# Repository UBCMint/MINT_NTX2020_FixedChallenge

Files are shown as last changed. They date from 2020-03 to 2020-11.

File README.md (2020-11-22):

# MINT EEG Acquisition System: JellyFish 1.0

## Background
There are many commercially available EEG headsets such as MUSE, OpenBCI, Neurosky, and Emotiv. However, they have too high price, not enough electrodes for high EEG spatial-resolution, low signal quality, or too much time to set up. Over the last two years, MINT has mainly focused on the EEG board only. This year, we will integrate the EEG board into a complete EEG headset that is comfortable, adjustable, sturdy to be worn anytime and anywhere at a reasonable price so that EEG headset can become a common household device as a computer mouse.

## Overall Design

## Headset Design
One of the primary issues that needed to be tackled was being able to adjust the headset to various headsizes. On top of this, our headset needed to be able to conform to the 10-20 system for electrode placement. This was done by using three headbands that go across the head. These headbands each contain rails which the electrodes lock onto. Additionally, to deal with the various head circumferences available, an elastic band is placed across the forehead, attaching the two ends of the headset, allowing for various headsizes to be used with different elastic bands and allowing the headset remain stable. This allows for the electrodes to be placed anywhere along the head thus conforming to all head sizes.

In our final design it was determined that a fluid source was needed to ensure that the electrodes were saturated at all times in order to deliver the best result. This was done by creating a tank at the top of the head which holds said fluid. One key concern of having this fluid was that we knew that it would conduct the signal throughout the solution and with that, we needed to design a system that not only held the fluid but also distributed the solution separately to each electrode. From this, it was determined that a rotating mechanism was the best solution in that every couple hours an individual would need to rotate the lid to the holder in order to distribute the fluid.

In addition to the central fluid tank holder, another method for solution distribution has been made. In this solution, rather than having tubes branching from a central tank, each electrode would possess its own mini-tank that would easily connect and disconnect to refill (similar to filling a toy water gun). This method requires more testing. However if successful, may allow for more fluid to be stored in the system as a whole.

The final aspect to this headset is the board holder located in the back of the head. This unit combines both the battery for the circuit as well as the circuit board in a protected location with holes conveniently located for any required connections or buttons. Additionally, this boardbox will be wrapped in sheet metal to minimize any electromagnetic radiation that may be present in the area. This allows all processing and power of the headset to be located in one location. 

## Electrode
The wet electrode consists of a piece of cotton sandwich between the scalp and the pre-amplifier PCB board that acts as a bridge when saturated with the electrode solution. Active electrodes with pre-amplifiers allow for the signal acquired to be immediately boosted before additional noise is incorporated into the signal during the travel between the electrode and the system. The signal can be further increased by a screw on top of the electrode that increases the pressure between the cotton and the scalp when twisted. Handles on the sides of the electrode allows for the component to be mounted and slide on the headset frame for maximum flexibility.

## EEG Board: MENTHA 3.0

## Budget
Below is the rough breakdown of costs, for those who want to replicate this design:  
~$0.5 for consumable cotton pieces and salt.  
~$1.50 for fluid tank & board holder (PLA)  
~$0.12 for each electrode (PLA)  
~$3.25 for headset frame (TPU)  

## About Us

JellyFish 1.0 was created by [(Multifaceted Innovation in NeuroTechnology](https://ubcmint.github.io/) (MINT), an undergraduate neurotech team, part of the group [Biomedical Engineering Student Team](http://www.ubcbest.com/) at the University of British Columbia in Vancouver, Canada.

JellyFish 1.0 was submitted as a project for the Fixed Challenge category of the [NeuroTechX 2020 Student Club competition](https://neurotechx.github.io/studentclubs/competition/).

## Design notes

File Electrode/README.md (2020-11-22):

# MINT EEG Electrode Evolution Summary 

## Electroplated Electrodes (Dry)
The electroplating electrodes use a mixture of Ag/AgCl or silver paint  (SCP03B) solution to plate the surface of the electrodes. Several electrode shapes and designs were explored to determine optimal configuration for effective signal collection and high signal:noise reading. These electrodes can record alpha rhythms correctly, but it has been noted that signals collected by the electrodes have a higher noise and impedance compared to the traditional Ag/AgCl electrodes. Additionally, coating begins to wear off after approximately 100 scratches. The scratches can be remend by recoating the electrodes with the silver solution. Although electroplated electrodes can measure alpha waves, the concept was abandoned due to its low signal:noise ratio and durability.

## Regenerated Cellulose Membranes Electrodes (Dry)
Regenerated cellulose membrane electrodes are identified to be suitable for long term use due to regenerative properties as well as high porosity for high surface area. Flower paper was identified to have regenerated cellulose membrane properties. The electrodes were soaked in an electrolyte solution of eight packs of table salt dissolved in water. After conducting eight impedance measurements, a high impedance average was found. Due to the identified high impedance, the regenerated cellulose membrane electrodes were not fully developed. 

## Conductive Fabric Electrodes (Dry)
The developed conductive fabric electrode electrodes use a 3x3x1.5cm cube packaging foam as a core, wrapped in a sheet of woven, silver, conductive fabric. The electrode provides comfort to the user as well as allowing electrodes to contour the head. However, the fabric electrode was calculated to have high impedance in addition to visual wear-and-tears to the fabric. Despite the comfortability and contouring capabilities, the conductive fabric electrodes were not fully developed due to a high impedance and low durability.

## Dry Spring Electrodes (Dry)
Dry spring electrodes incorporated springs into dry finger electrodes to better contour the head. Samples from an MDPI article were requested to analyze spring electrodes. Upon testing, the required pressure and flexibility could not be achieved and the electrodes were deemed to be uncomfortable or painful. Although impedance was not recorded, the idea was scrapped due to high discomfortability from high spring constant.

## Compression Fabric Electrodes (Dry)
Similar to the conductive fabric, a pressure-sensitive conductive sheet (velostat/linqstat) is used in lieu of the conductive fabric. The conductive material has a resistance reducing property when pressure is applied to the fabric, which can be useful for designing flexible sensors. The pressure also allows the electrode to better contour to the head and maximize surface area for signal acquisition. However, upon testing, the compression fabric is found to be twice as large as the conductive fabric, despite applying large pressure. Additionally, after several uses, oily residue begins to accumulate on the surface of the fabric. This suggests a quick and easy formation of biofilms, which may require additional maintenance from the user. Failure to manage the electrodes may impose health risk onto the user. Therefore, the compression fabric is rejected due to its high impedance and potential health issues.

## Cotton Electrodes (Hybrid)
The current design looks at creating a hybrid electrode which uses cotton and electrolyte solution to bridge the connection between the scalp and PCB board. The cotton will be connected to a water tank that contains dissolved salt. Adding pressure onto the cotton allows more of the liquid to spread onto the scalp, maximizing surface area for signal acquisition. Conducting impedance tests show that cotton soaked in solution has a significantly lower impedance than dry or wet OPENBCI electrodes. Therefore, the hybrid cotton electrodes were further developed for the 2020 MINT EEG acquisition system. 

## Extensive writeup of past designs can be found on the [team’s Google Drive](https://docs.google.com/document/d/16VlDZtCEF2bn4U8mC6i96VPIYXMff-jvLBDzw5MMWTI/edit#heading=h.276hzmhpmpdi)

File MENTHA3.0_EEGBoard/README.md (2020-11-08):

# MINT_EEGBoard: MENTHA 3.0

### Background
The goal of MENTHA is to design a board that can collect EEG potentials accurately and effectively. MENTHA 3.0 will utilize a PIC32MX microcontroller to send data acquired from the specialized biopotential measurement device (ADS1299) to a PC, where the data will be analyzed and live plotted.

The choice to use these components were based on research which showed the prevalence of the ADS1299 in literature. Additionally, MINT wanted to develop a smaller and more compact design than previous submissions.

## Electrical

### Initial concept
The initial concept was to use a similar approach as to previous years. That being implementing instrumentation amplifiers, along with active filters in order to acquire our signal. 

After testing with various amplifiers and topologies, performing some research, and receiving input from colleagues, the choice was made to use the ADS1299 chip with passive and software filters instead. The ADS1299 is low noise and can measure small voltages, which is important for biopotential measurements  

### ADS1299
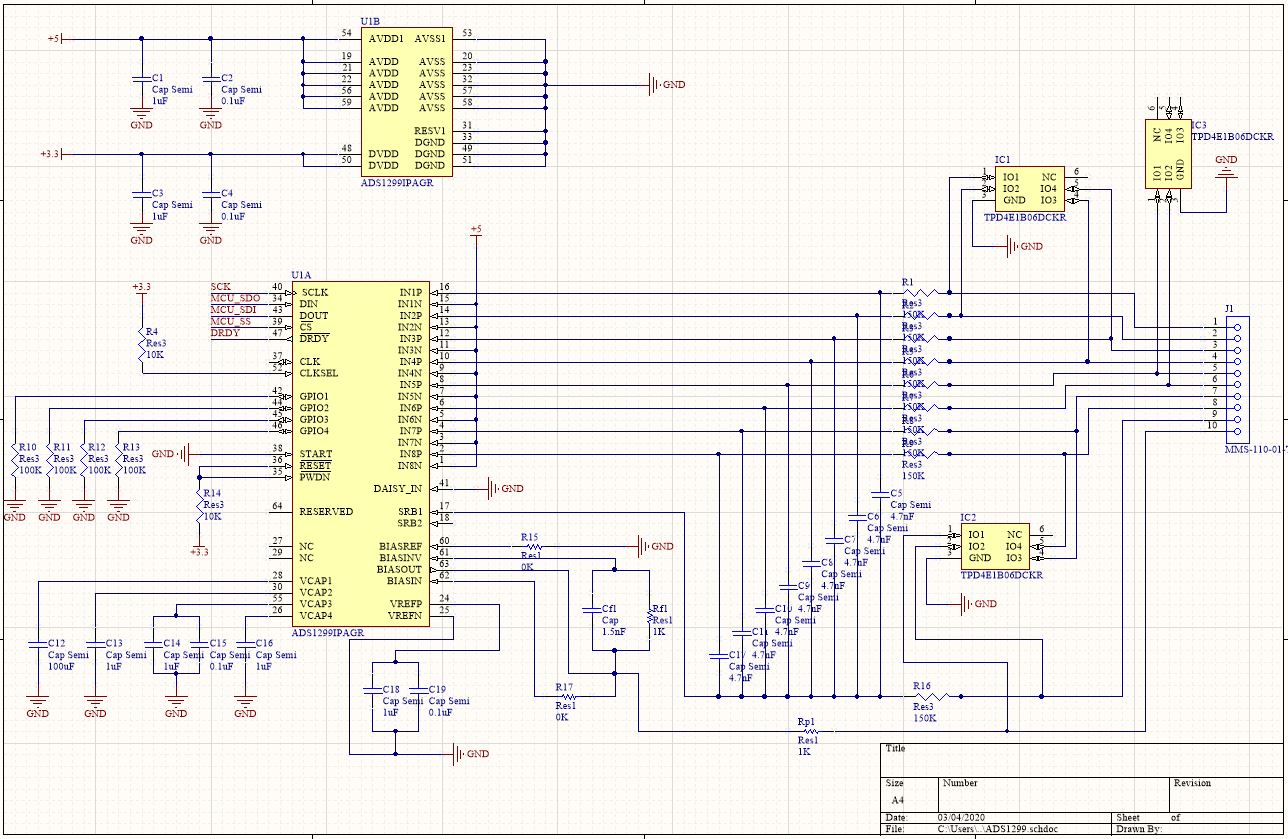
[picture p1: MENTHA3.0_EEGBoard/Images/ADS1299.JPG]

We have set up the ADS 1299 with a referential montage and as such, each of the 8 input channels have the same reference electrode. We implemented a differential passive low pass filter at 160Hz (see bode plot). This lets us remove high frequency signals without introducing more noise to the system or losing signal in 10-50Hz rage. Furthermore, the differential set up of the filter rejects common signals between the electrode signal and the reference ground and therefore removes common noise and DC noise. The ADS1299 is connected to the microcontroller with and SPI interface.

Bode plots and frequency specifics?

### Microcontroller
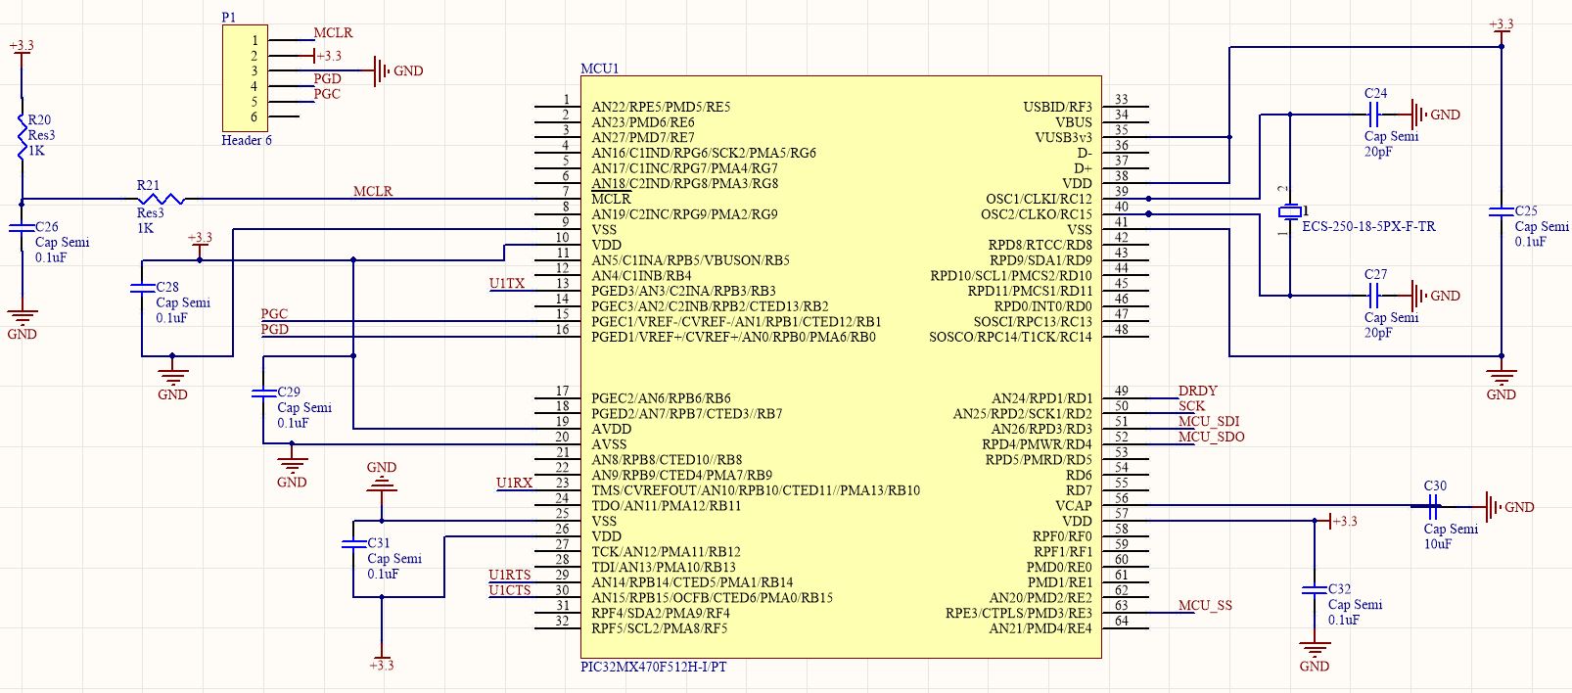
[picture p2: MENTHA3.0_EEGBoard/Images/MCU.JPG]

The PIC32MX450/470 is being utilized for this project. The microcontroller was chosen due to its relatively fast clock speed, large memory size, and numerous peripheral pins. Additionally, Microchip offers easy solutions for programming and debugging using the PICkit3 and their MPLAB X IDE. The device is programmed using the PICKit3 through the pins labeled MCLR, PGD, and PGC. Attached to our MCU we have a 25MHz oscillator to set the clock speed, an FT232R USB UART IC for PC data transfer, connections to the ADS1299 through SPI, and the various required connections and decoupling capacitors.

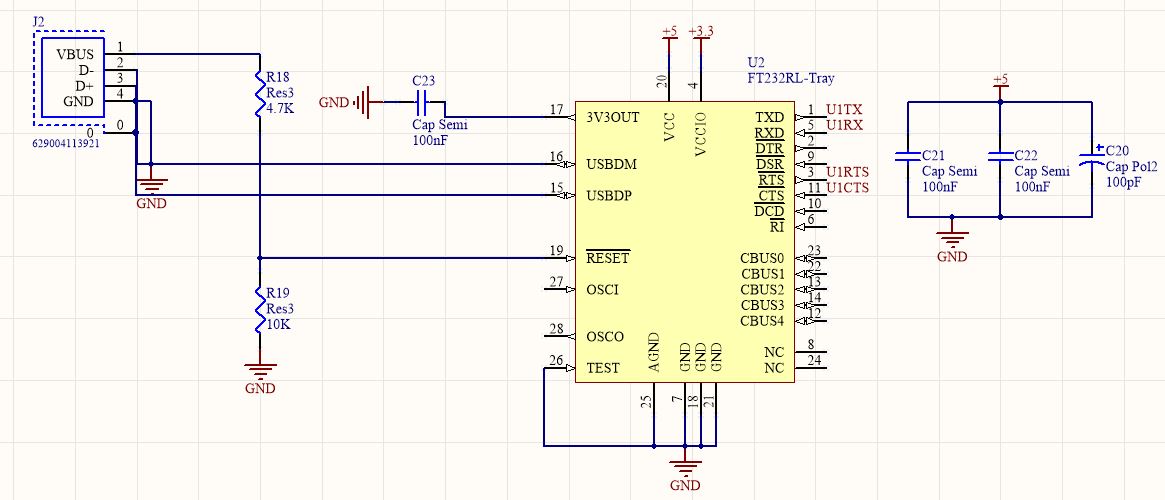
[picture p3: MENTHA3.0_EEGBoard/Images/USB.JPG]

To interface with a PC for data transfer, we have implemented an FT232R USB UART IC. This device connects to the UART peripherals of the PIC32 in order to transfer data to and from a PC with a wired USB-A connection. We have configured the FT232R chip in a self powered configuration as acording to the IC datasheet.

### Power Electronics
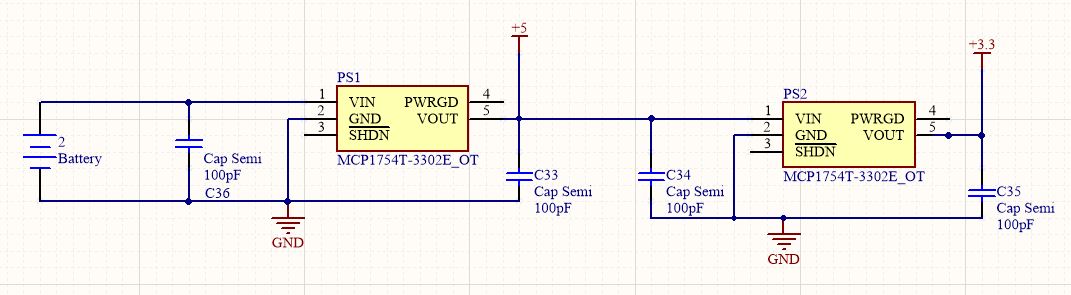
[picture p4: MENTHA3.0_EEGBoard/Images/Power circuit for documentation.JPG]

The Power electronics for the board offers two power rails using two voltage regulators. One is used to create a 5V rail from the input battery or power supply connection. The other is used to create a 3.3V rail and uses the 5V rail as an input.

## PCB Layout
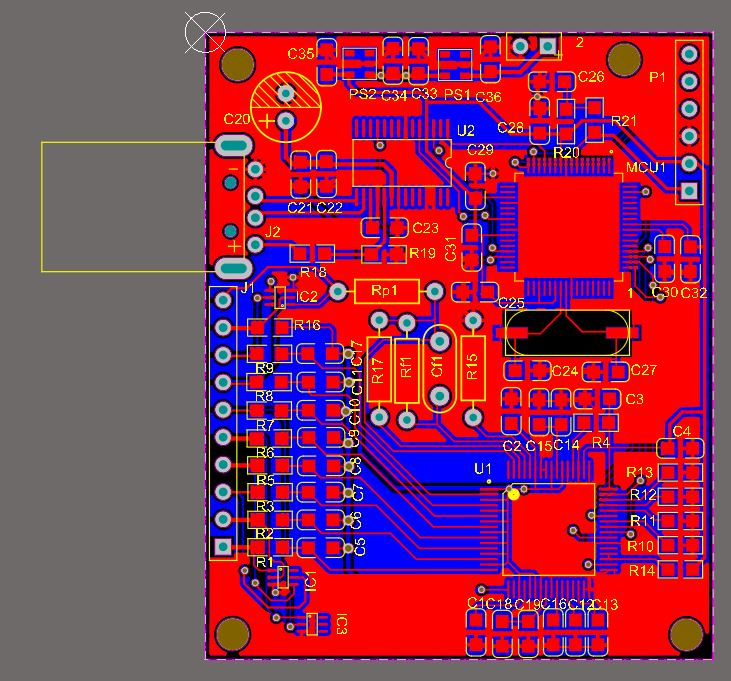
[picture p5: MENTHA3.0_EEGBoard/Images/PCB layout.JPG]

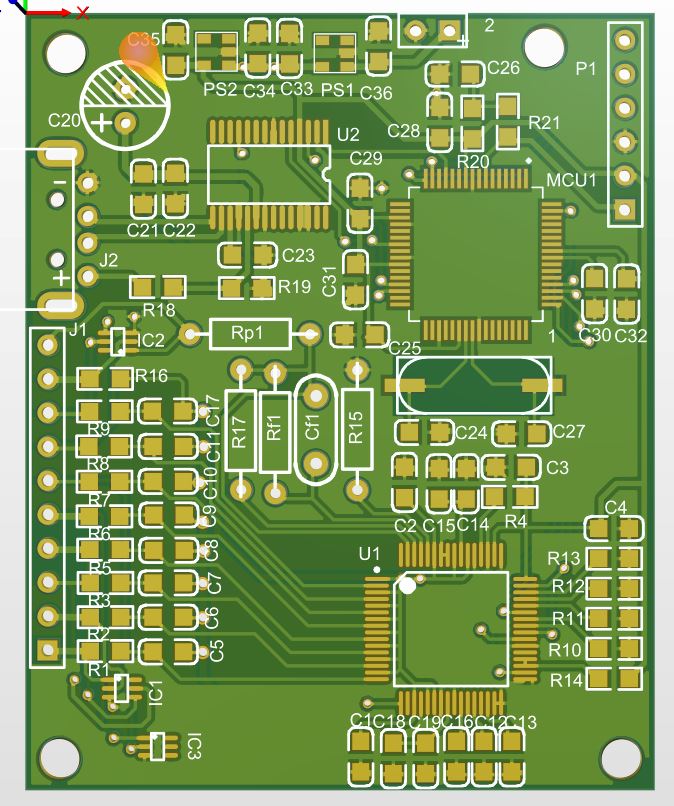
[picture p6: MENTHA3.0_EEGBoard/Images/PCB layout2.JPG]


### Note: 
Due to the global outbreak of COVID-19 the electrical sub team has been limited in our access to resources required to finish and test the electrical components of the EEG acquisition board.

## Software

### Board Firmware
Unfinished - see programminginfo.txt

### Data processing (PC)
Unfinished

### Note:
Due to the global outbreak of COVID-19 the electrical sub team has been limited in our access to resources required to finish the EEG acquisition board, and thus have been limited in firmware and software development.

## Budget
Below is the rough breakdown of costs, for those who want to replicate this design:

---

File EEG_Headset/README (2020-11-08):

Hello!

This is the folder containing all the past iterations and current updates of the Jellyfish headset. 

Below are some of the features of the headset, which can also be found in the STL files. 

Adjusting Head Size Mechanism:
In order to effectively accommodate all head sizes, we have implemented an adjustable mechanism that runs both around the head and across it. For the component that wraps around the front of the head, an elastic band stretched around the front of the head will be used to apply suitable pressure for the given head size. Across the head, each band will be either bolted or held using electrodes to the first band. In doing so, all head sizes will be accommodated. Additionally, since our team is utilizing the 10-20 system for electrode placement, it was a requirement that each electrode could be moved at any given time. This is done using a screw on design that will further be explained below

Board Box:
The board box that connects to the headset is quite simple. It consists of two parts held together by a rod which, when inserted, allows the box to hinge. Inside the box, there are 4 extrusions that will snuggly fit into the board itself. Additionally, the box will be wrapped in aluminum tape as to create a sort of Faraday cage, this reducing electromagnetic noise which is important considering the signals found are quite small and susceptible to noise. Finally, there are two holes along the side of the box to allow access to power and pins at any given time. 
Easily open and remove the board.
Protect the board from physical force and also electromagnetic noises (alumni tape…)
Fluid Tank - Natalia
Saline Electrode
How we ensure the saline can be refilled and distributed to all electrodes.

Electrode:
The wet electrode consists of a piece of cotton sandwich between the scalp and the pre-amplifier PCB board that acts as a bridge when saturated with the electrode solution. Active electrodes with pre-amplifiers allow for the signal acquired to be immediately boosted before additional noise is incorporated into the signal during the travel between the electrode and the system. The signal can be further increased by a screw on top of the electrode that increases the pressure between the cotton and the scalp when twisted. Handles on the sides of the electrode allows for the component to be mounted and slide on the headset frame for maximum flexibility.
Pre-amplifier PCB + connections to wire
Connect it to the frame so that it’s movable 
Adjust the pressure of electrode

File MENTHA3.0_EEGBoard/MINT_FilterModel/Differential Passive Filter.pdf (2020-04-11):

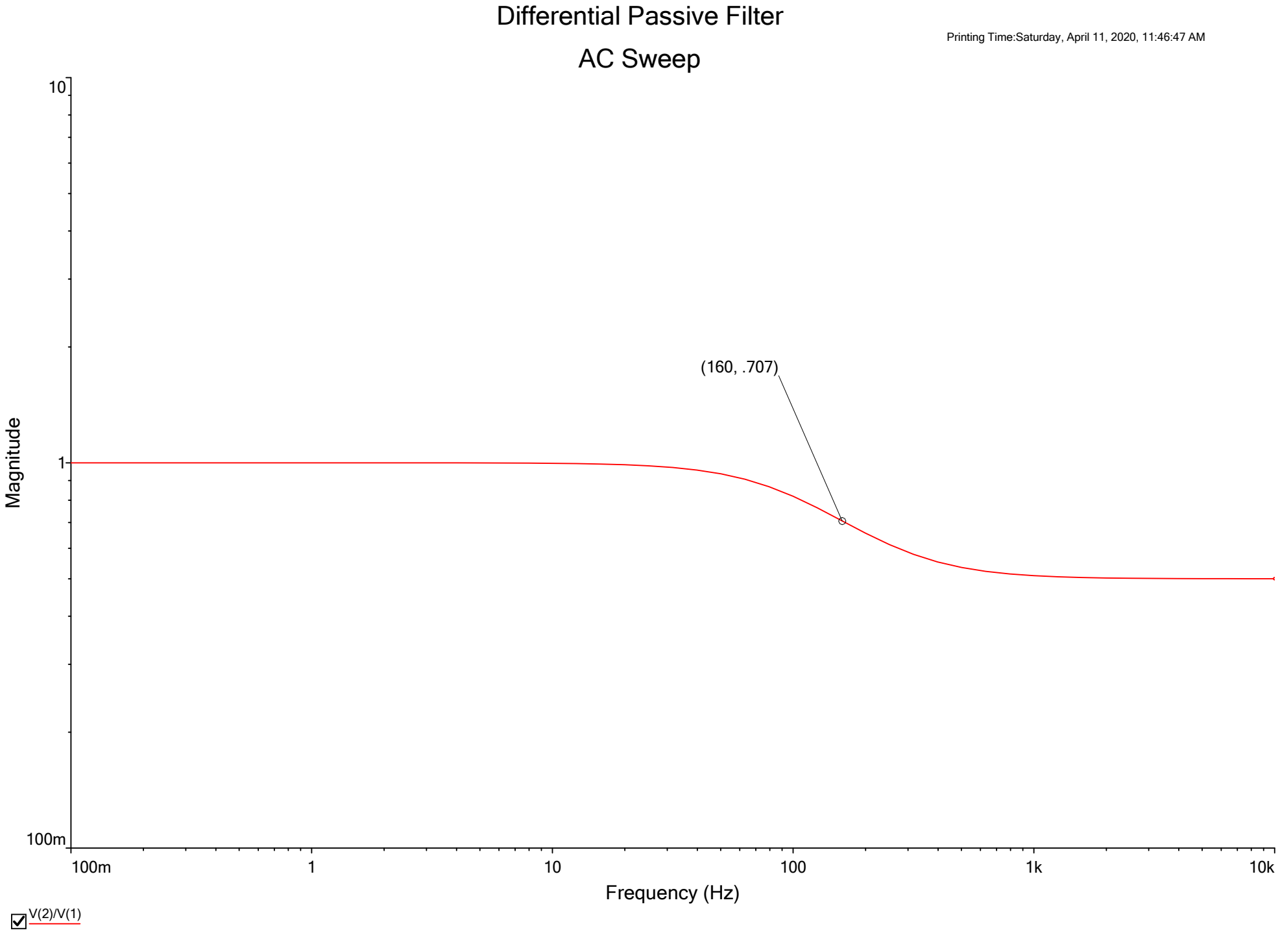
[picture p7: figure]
Differential Passive Filter; AC Sweep; Frequency (Hz); 10k Magnitude

Printing Time:Saturday, April 11, 2020, 11:46:47 AM

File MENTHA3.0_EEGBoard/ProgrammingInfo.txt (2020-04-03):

FIRMWARE LOCATION: MINT_EEGAcquisitionSystem/MINT_EEGFirmware/MINT_EEG_Firmware.X/

TOOLS USED:
1.MPLAB X IDE
2.MPLAB XC32 compiler
3.legacy peripheral libraries (V1.42)
4.PICKit3

INSTALLATION PROCESS:
1. Download MPLAB X IDE, MPLABX IPE, and the XC32 compiler (not sure if the compiler is necissary as we want to use an older version anyway that I think comes with the IDE). 

2. Seperately download the legacy peripheral libraries and place them in the V1.42 folder (wherever that is saved in your computer). 

3. Open the project in MPLAB X IDE and try a clean and build of the base project.

TO DO (Unfinished for project):
-Embed device's configuration bits into code.
-Add interrupt vectors to interrupt.c (if interrupts are to be used).
-Define system parameters (such as operating frequency) to system.h.
-Add user level functions to user.h and user.c (initialize I/O, user peripherals like the ADS1299, computations, ect.)
-Add code to main.c (initialization and main loop).
-Document code in project_information.txt.
-Test on actual hardware (Board unfinished due to COVID-19 issues)

THE FOLLOWING ARE RESOURCES THAT MAY ASSIST IN PROGRAMMING THE PIC32MX450F256H:
Found some sample code we can use to implement SPI on the PIC32MX470: 
https://www.microchip.com/forums/m929006.aspx, 
http://hades.mech.northwestern.edu/index.php/PIC32MX:_SPI_Communication_between_PIC32s

and section 10.1.2 in this datasheet: 
https://www.ti.com/lit/ds/symlink/ads1299.pdf sets up the ADS1299 for basic functions

An examples project shows code to write in MPLab for the PIC: 
https://www.elprocus.com/pic-microcontroller-programming-using-c-language/

Setting up PIC programmer example:
https://www.canakit.com/Media/Manuals/UK1300.pdf

Code examples for the PIC Xpress board!!
https://mplabxpress.microchip.com/mplabcloud/example

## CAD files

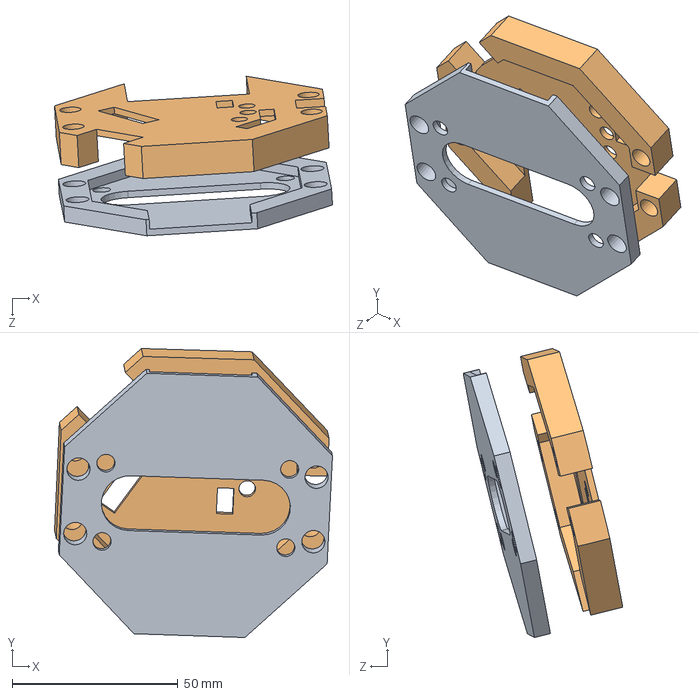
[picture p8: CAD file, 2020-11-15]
EEG_Headset/Base Board/BaseboardAssembly.SLDASM
83.8 x 87.2 x 48.1 mm
Top board
Base board pt 3

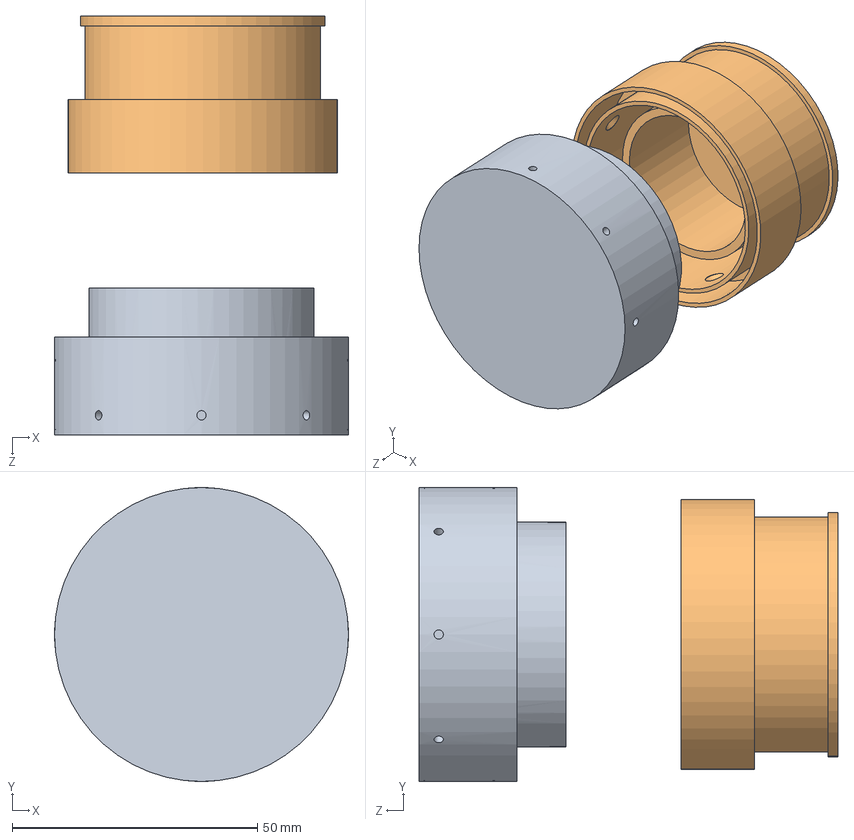
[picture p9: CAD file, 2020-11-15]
EEG_Headset/Fluid Container/Container_Assembly.SLDASM
60.0 x 60.0 x 85.5 mm
Fluid Holder
Container_Lid

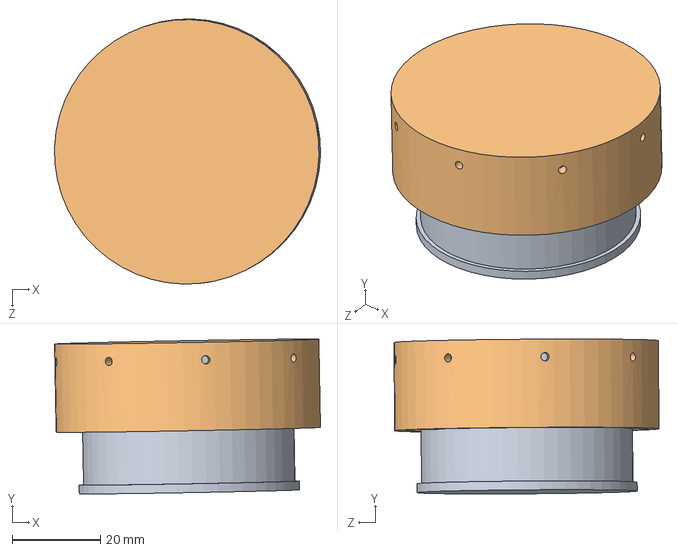
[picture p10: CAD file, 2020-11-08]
Electrode/CADs/Frame/Jellyfish_Assembly1.SLDASM
60.3 x 35.1 x 60.1 mm
Container_Lid
Fluid Holder

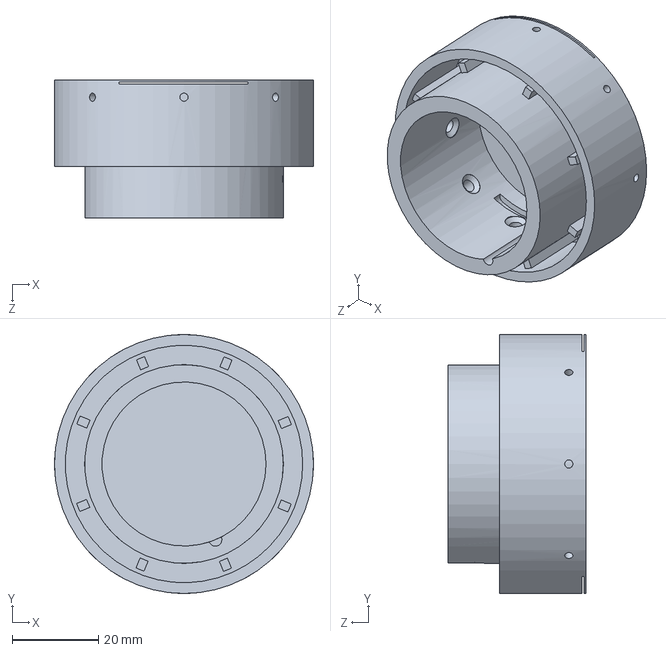
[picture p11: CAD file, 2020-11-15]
EEG_Headset/Fluid Container/Container_Base.SLDPRT
60.0 x 60.0 x 32.0 mm

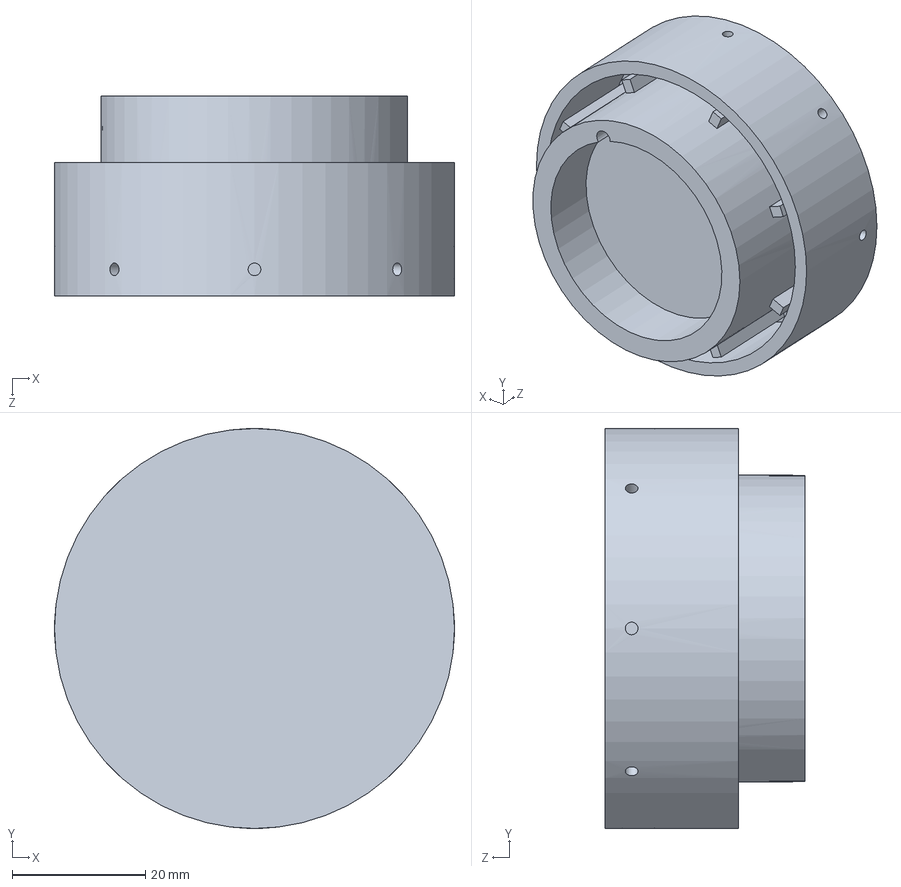
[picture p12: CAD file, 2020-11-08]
Electrode/CADs/Frame/Fluid Holder.SLDPRT
60.0 x 60.0 x 30.0 mm

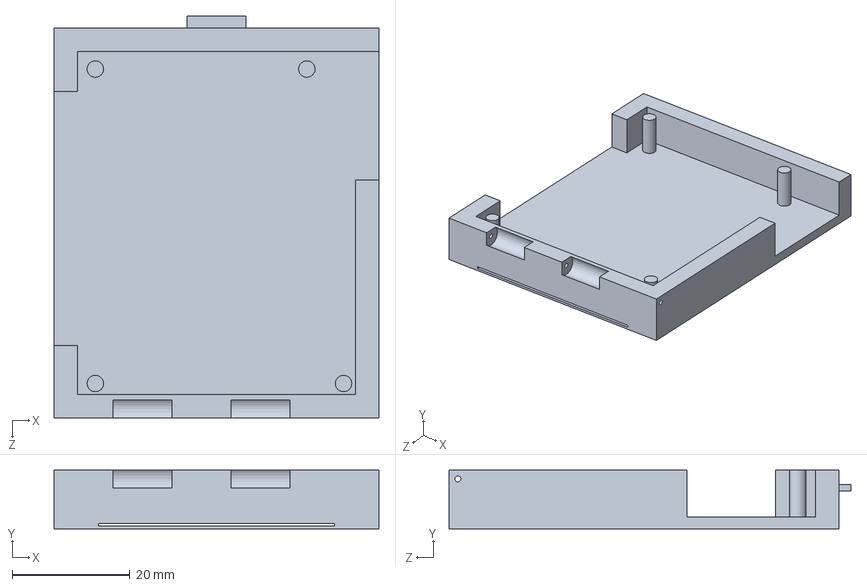
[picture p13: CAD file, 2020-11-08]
Electrode/CADs/MENTHA3.0 Box/new board holder.SLDPRT
55.1 x 10.0 x 68.2 mm

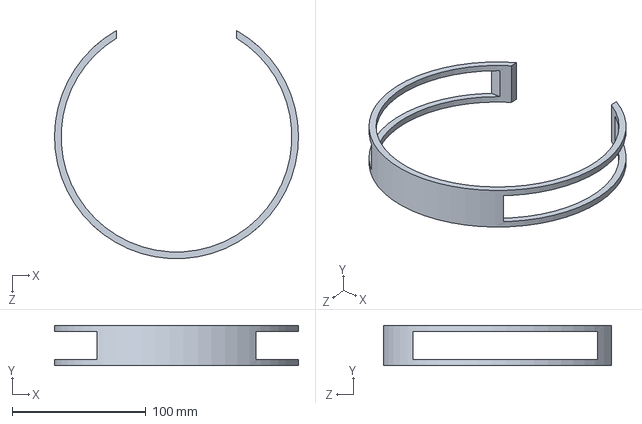
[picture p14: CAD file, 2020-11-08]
Electrode/CADs/Frame/headset pt1.SLDPRT
182.7 x 30.0 x 170.7 mm

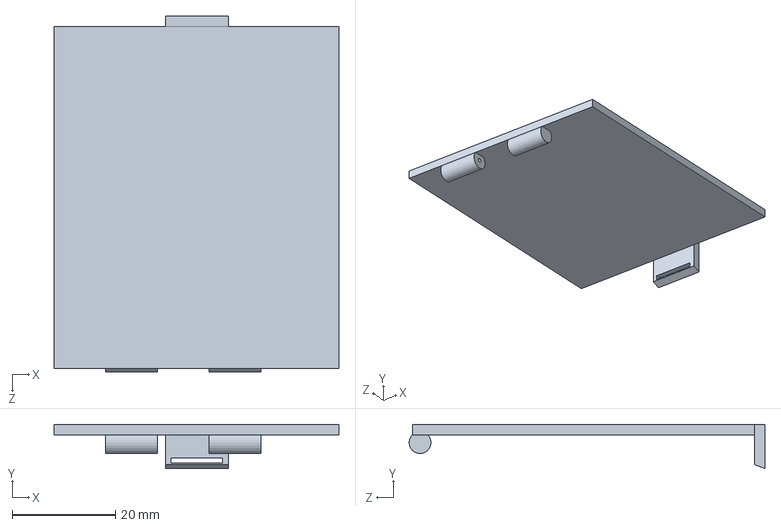
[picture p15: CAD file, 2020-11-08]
Electrode/CADs/MENTHA3.0 Box/New lid.SLDPRT
55.1 x 8.52 x 68.8 mm

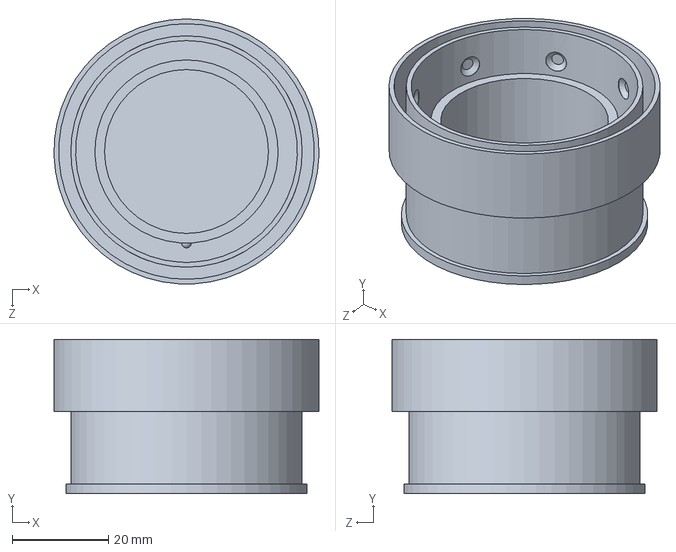
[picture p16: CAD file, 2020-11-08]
EEG_Headset/Fluid Container/Container_Lid.SLDPRT
55.0 x 32.0 x 55.0 mm

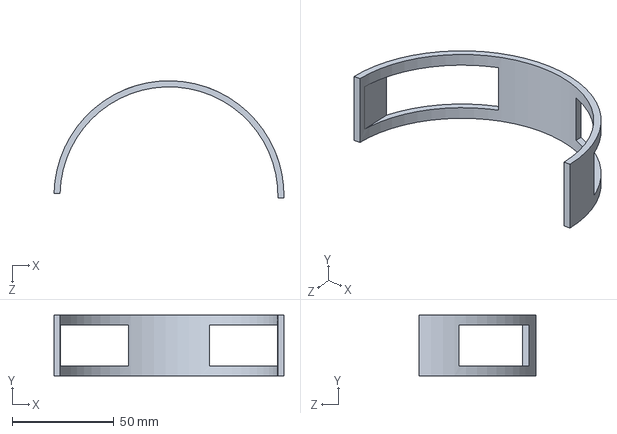
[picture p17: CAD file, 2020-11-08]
Electrode/CADs/Frame/headset pt3.SLDPRT
113.3 x 30.0 x 57.8 mm

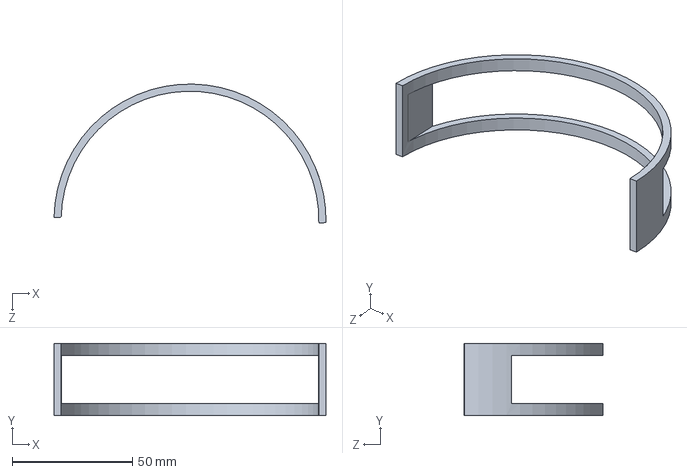
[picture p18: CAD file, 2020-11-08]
Electrode/CADs/Frame/headset pt2.SLDPRT
113.3 x 30.0 x 57.8 mm

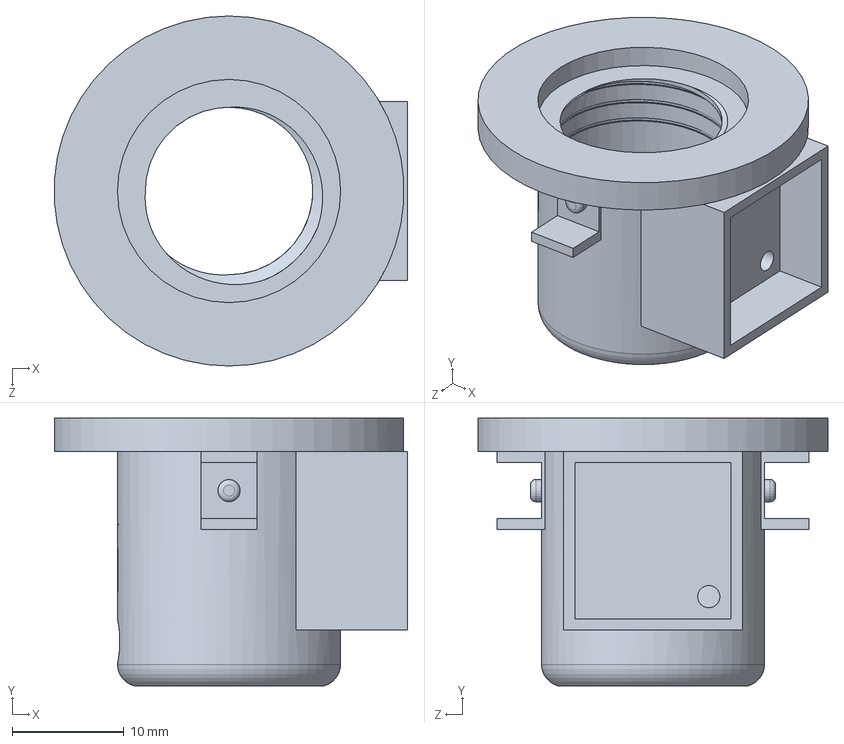
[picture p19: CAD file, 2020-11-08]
Electrode/CADs/Electrode/Screw-Type Electrode (Bot).SLDPRT
31.7 x 24.0 x 31.4 mm

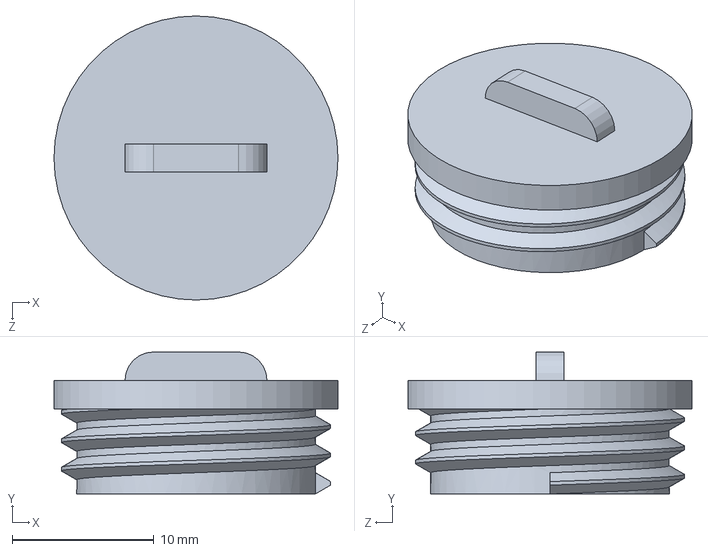
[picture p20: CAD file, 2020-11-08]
Electrode/CADs/Electrode/Screw-Type Electrode (Top).SLDPRT
20.0 x 10.0 x 20.0 mm

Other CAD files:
Electrode/CADs/Electrode/Screw-Type Electrode (Bot).STL
Electrode/CADs/Electrode/Screw-Type Electrode (Top).STL
Electrode/CADs/MENTHA3.0 Box/new board holder.STL

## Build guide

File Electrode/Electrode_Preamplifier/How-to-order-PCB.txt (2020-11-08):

How to Order PCB

Please refer to:
https://docs.easyeda.com/en/PCB/Order-PCB

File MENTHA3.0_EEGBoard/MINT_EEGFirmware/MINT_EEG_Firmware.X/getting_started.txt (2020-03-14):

This is a general template for the PIC32 family of microcontrollers.  It's
purpose is to provide a project shell for users to get started designing their
own applications.  Final qualification and testing of this project is left to
the user.

ADVANCED USER TIP

From the main menu, refer to the Task list by going to Window > Tasks (Ctrl+6).
As long as the task window is not configured to filter out any tasks,
the getting started TODO list embedded in this project will be displayed.

Make sure the 'Show tasks for the main project and for the open projects which
depend on it' option is selected on the left hand side of the Tasks window so
that tasks related to other projects are not active.

HOW TO ADD YOUR OWN CODE TO A TEMPLATE

STEP 1

First install the appropriate C compiler if you have not done so already.

See www.microchip.com/compilers

Next, build this project by clicking the Clean and Build Icon (the hammer and
broom symbol) in the MPLAB X IDE Toolbar.  If this project builds, then you are
ready to make changes for your own application.  If the project does not build,
you need to troubleshoot why the project does not build before moving on.

STEP 2

Embed your device's configuration bits into the code.  Instructions for this
are commented in configuration_bits.c

STEP 3

Unless interrupts are not used in your application, add the interrupt vectors
you intend to use to interrupts.c.  Code stubs are provided in interrupts.c.
Make sure that you check the device datasheet to confirm that the interrupt
you are using is present in the device selected, and check the device .h
file for the most up to date list of interrupt vector mnemonics.

STEP 4

Define system parameters such as the system operating frequency in system.h.

Add system level functions to system.h and system.c.  For example, if
you want a function to determine the reset source of the device to know if you
need to backup data, do an oscillator switch, enter a low power mode, etc...
these types of functions may be added to system.c and prototypes can go in
system.h.

STEP 5

Add user level functions to user.h and user.c.  User level functions are
functions that initialize I/O, initialize user peripherals like the ADC,
compute user algorithms, perform calculations on sampled user data, and so on.
User function prototypes and macros may be placed in user.h, and user
functions themselves may go in user.c

STEP 6

Add code to main.c on the line that says <INSERT USER APPLICATION CODE HERE>.
For example, here you would call functions in user.c or system.c, or possibly
setup your own state machine or primary code loop.

Global variables may be added to main.c as well.  As a general practice, macros
and prototypes may go in header files, but variable declarations should not
go in .h files.  Variable declarations should be placed in .c files.

STEP 7

Design the rest of your application.  Add new files to the application, and
test the finished product.

STEP 8

Document what the project does and include other project information in
project_information.txt.

KNOWN ISSUES

This message may appear after a successful build:

Configuration Bits: address 0x1FC02FF0: USERID = 22136 does not match any valid
value in the device database.  Setting it to the default value.

To avoid this message, the USERID may be embedded in the device as follows:

const int __attribute__((section(".config_BFC02FF0"))) configword_2ff0 = 0x12345678u;

(Adjust the address appropriately for the device in use if needed).

There will someday be a less painful way of embedding the USERID.  Until then,
this is how it can be done.

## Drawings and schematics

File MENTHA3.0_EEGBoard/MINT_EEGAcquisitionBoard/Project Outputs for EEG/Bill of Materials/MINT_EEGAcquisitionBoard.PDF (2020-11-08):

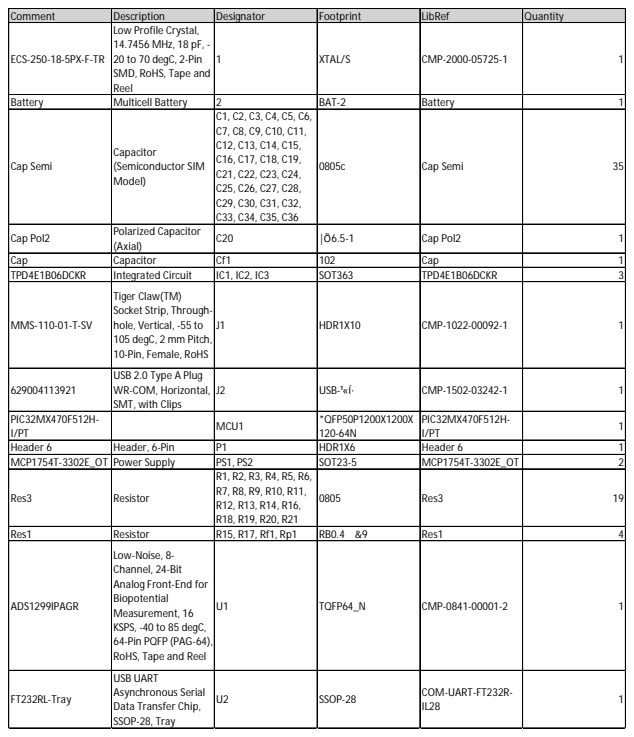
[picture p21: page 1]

Comment | Description | Designator | Footprint | LibRef | Quantity
ECS-250-18-5PX-F-TR | Low Profile Crystal, 14.7456 MHz, 18 pF, -20 to 70 degC, 2-Pin SMD, RoHS, Tape and Reel | 1 | XTAL/S | CMP-2000-05725-1 | 1

Battery | Multicell Battery | 2 | BAT-2 | Battery | 1
Cap Semi | Capacitor (Semiconductor SIM Model) | C1, C2, C3, C4, C5, C6, C7, C8, C9, C10, C11, C12, C13, C14, C15, C16, C17, C18, C19, C21, C22, C23, C24, C25, C26, C27, C28, C29, C30, C31, C32, C33, C34, C35, C36 | 0805c | Cap Semi | 35

Cap Pol2 | Polarized Capacitor (Axial) | C20 | |Õ6.5-1 | Cap Pol2 | 1

Cap | Capacitor | Cf1 | 102 | Cap | 1
TPD4E1B06DCKR | Integrated Circuit | IC1, IC2, IC3 | SOT363 | TPD4E1B06DCKR | 3

MMS-110-01-T-SV | Tiger Claw(TM) Socket Strip, Through-hole, Vertical, -55 to 105 degC, 2 mm Pitch, 10-Pin, Female, RoHS | J1 | HDR1X10 | CMP-1022-00092-1 | 1

629004113921 | USB 2.0 Type A Plug WR-COM, Horizontal, SMT, with Clips | J2 | USB-¹«Í· | CMP-1502-03242-1 | 1

PIC32MX470F512H-I/PT | | MCU1 | *QFP50P1200X1200X 120-64N | PIC32MX470F512H-I/PT | 1

Header 6 | Header, 6-Pin | P1 | HDR1X6 | Header 6 | 1
MCP1754T-3302E_OT | Power Supply | PS1, PS2 | SOT23-5 | MCP1754T-3302E_OT | 2
Res3 | Resistor | R1, R2, R3, R4, R5, R6, R7, R8, R9, R10, R11, R12, R13, R14, R16, R18, R19, R20, R21 | 0805 | Res3 | 19

Res1 | Resistor | R15, R17, Rf1, Rp1 | RB0.4 &9 | Res1 | 4

ADS1299IPAGR | Low-Noise, 8-Channel, 24-Bit Analog Front-End for Biopotential Measurement, 16 KSPS, -40 to 85 degC, 64-Pin PQFP (PAG-64), RoHS, Tape and Reel | U1 | TQFP64_N | CMP-0841-00001-2 | 1

FT232RL-Tray | USB UART Asynchronous Serial Data Transfer Chip, SSOP-28, Tray | U2 | SSOP-28 | COM-UART-FT232R-IL28 | 1

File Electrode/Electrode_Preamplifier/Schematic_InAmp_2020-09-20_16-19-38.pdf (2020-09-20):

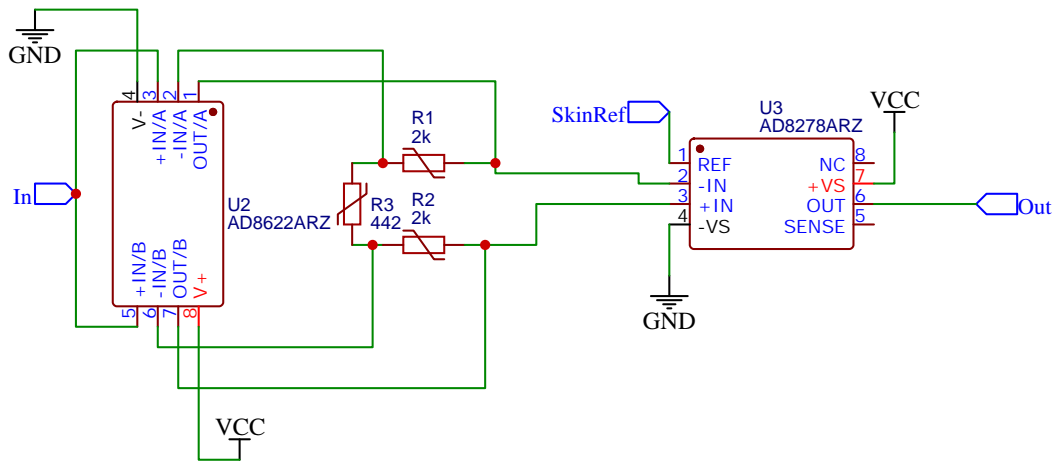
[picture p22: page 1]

Drawn By: kylem.workemail

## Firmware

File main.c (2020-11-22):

/******************************************************************************/
/*  Files to Include                                                          */
/******************************************************************************/
// PIC32MX460F512L Configuration Bit Settings

// DEVCFG3
#pragma config USERID = 0xFFFF          // Enter Hexadecimal value (Enter Hexadecimal value)
#pragma config FSRSSEL = PRIORITY_7     // Shadow Register Set Priority Select (SRS Priority 7)
#pragma config PMDL1WAY = ON            // Peripheral Module Disable Configuration (Allow only one reconfiguration)
#pragma config IOL1WAY = ON             // Peripheral Pin Select Configuration (Allow only one reconfiguration)
#pragma config FUSBIDIO = ON            // USB USID Selection (Controlled by the USB Module)
#pragma config FVBUSONIO = ON           // USB VBUS ON Selection (Controlled by USB Module)

// DEVCFG2
#pragma config FPLLIDIV = DIV_2         // PLL Input Divider (2x Divider)
#pragma config FPLLMUL = MUL_20         // PLL Multiplier (20x Multiplier)
#pragma config UPLLIDIV = DIV_2         // USB PLL Input Divider (2x Divider)
#pragma config UPLLEN = OFF             // USB PLL Enable (Disabled and Bypassed)
#pragma config FPLLODIV = DIV_4         // System PLL Output Clock Divider (PLL Divide by 4)

// DEVCFG1
#pragma config FNOSC = FRCPLL           // Oscillator Selection Bits (Fast RC Osc with PLL)
#pragma config FSOSCEN = OFF            // Secondary Oscillator Enable (Disabled)
#pragma config IESO = OFF               // Internal/External Switch Over (Disabled)
#pragma config POSCMOD = OFF            // Primary Oscillator Configuration (Primary osc disabled)
#pragma config OSCIOFNC = ON            // CLKO Output Signal Active on the OSCO Pin (Enabled)
#pragma config FPBDIV = DIV_1           // Peripheral Clock Divisor (Pb_Clk is Sys_Clk/1)
#pragma config FCKSM = CSDCMD           // Clock Switching and Monitor Selection (Clock Switch Disable, FSCM Disabled)
#pragma config WDTPS = PS1048576        // Watchdog Timer Postscaler (1:1048576)
#pragma config WINDIS = OFF             // Watchdog Timer Window Enable (Watchdog Timer is in Non-Window Mode)
#pragma config FWDTEN = OFF             // Watchdog Timer Enable (WDT Disabled (SWDTEN Bit Controls))
#pragma config FWDTWINSZ = WINSZ_25     // Watchdog Timer Window Size (Window Size is 25%)

// DEVCFG0
#pragma config DEBUG = OFF              // Background Debugger Enable (Debugger is disabled)
#pragma config JTAGEN = OFF             // JTAG Enable (JTAG Disabled)
#pragma config ICESEL = ICS_PGx2        // ICE/ICD Comm Channel Select (ICE EMUC2/EMUD2 pins shared with PGC2/PGD2)
#pragma config PWP = OFF                // Program Flash Write Protect (Disable)
#pragma config BWP = OFF                // Boot Flash Write Protect bit (Protection Disabled)
#pragma config CP = OFF                 // Code Protect (Protection Disabled)

// #pragma config statements should precede project file includes.
// Use project enums instead of #define for ON and OFF.


#define _SUPPRESS_PLIB_WARNING //SurpressesPlib warnings

#ifdef __XC32
    #include <xc.h>          /* Defines special funciton registers, CP0 regs  */
#endif

#include <stdint.h>         /* For uint32_t definition                        */
#include <stdbool.h>        /* For true/false definition                      */

#include "system.h"         /* System funct/params, like osc/periph config    */
#include "user.h"           /* User funct/params, such as InitApp             */ 
#include "configuration_bits.c" 

/******************************************************************************/
/* Global Variable Declaration                                                */
/******************************************************************************/

/* i.e. uint32_t <variable_name>; */
#define U1RX_RPB10_INDEX 0b0110
#define U1TX_INDEX 0b0011
#define DRDY_INDEX 0b0000       // pin 49 - same as SCK?? 
#define MCU_SCI_INDEX 1b0000    // pin 51 - doesn't like that it starts with a 0, which should indicate input
#define MCU_SDO_INDEX 0b1000    // pin 52 
#define MCU_SS_INDEX 0b0111     // pin 63
#define SCK_INDEX 0b0000        // pin 50 - same as DRDY? 

void InitSPI(void) {
    RPD3Rbits.RPD3R = MCU_SCI_INDEX;
    RPD1Rbits.RPD1R = DRDY_INDEX;
    RPD4Rbits.RPD4R = MCU_SDO_INDEX;
    // RPD2bits.RPD2R = SCK_INDEX: 
    RPD2Rbits.RPD2R = SCK_INDEX;
    RPE3Rbits.RPE3R = MCU_SS_INDEX; 
    
    LATDbits.LATD1 = 1;         // Set chip select high (idle state)
     
//    IEC0bits.SPI1EIE = 0;       // SPI interrupts disabled
//    IEC0bits.SPI1RXIE = 0;
//    IEC0bits.SPI1TXIE = 0;
     
    SPI1CONbits.ON = 0;         // Turn off SPI module
     
    SPI1BUF = 0;                // Clear the receive buffer
     
    SPI1BRG = 33333;            // FSCK = 160 Hz 
     
    SPI1STATbits.SPIROV = 0;    // Clear overflow flag
     
     
    /* SPI1CON settings */
    SPI1CONbits.FRMEN = 0;      // Framed SPI support is disabled
    SPI1CONbits.SIDL = 0;       // Continue operation in IDLE mode
    SPI1CONbits.DISSDO = 0;     // SDO1 pin is controlled by the module
    SPI1CONbits.MODE16 = 1;     // 16 bit mode
    SPI1CONbits.MODE32 = 0;     // 32 bit mode 
    SPI1CONbits.CKP = 1;        // Idle state for clock is high, active state is low
    SPI1CONbits.CKE = 0;        // Output data changes on transition from idle to active
    SPI1CONbits.SSEN = 0;       // Not in slave mode
    SPI1CONbits.MSTEN = 1;      // Yes in master mode
    SPI1CONbits.SMP = 1;        // Input data sampled at the end of data output time
     
    SPI1CONbits.ON = 1;         // Turn module on
}


short WriteReadSPI(unsigned short i) {
    TRISDbits.TRISD1 = 0;           // Set the chip select low
    SPI1BUF = i;                    // Write to buffer for transmission
    while (!SPI1STATbits.SPIRBF);   // Wait for transfer to be completed
    TRISDbits.TRISD1 = 1;           // Set the chip select back high
    return SPI1BUF;                 // Return the received value
}


// See  https://www.digikey.com/eewiki/display/microcontroller/Getting+Started+with+the+PIC32+and+MPLAB+X
// for more explanation of UART config
void InitUART(void) {
    RPB3Rbits.RPB3R = U1TX_INDEX ;// Configure RPB3 pin as U1TX
    U1RXRbits.U1RXR = U1RX_RPB10_INDEX; // Configure RPB10 pin as U1RX
    
    U1MODEbits.BRGH = 0; // Turn on UART1 module
    U1BRG = 129; // Set Baud Rate; 129 corresponds to 9600. See article above for formula
    
    U1MODEbits.SIDL = 0;                // Continue operation in SLEEP mode
    U1MODEbits.IREN = 0;                // IrDA is disabled
    U1MODEbits.RTSMD = 0;               // U1RTS pin is in Flow Control mode
    U1MODEbits.UEN = 0b00;              // U1TX, U1RX are enabled
    U1MODEbits.WAKE = 1;                // Wake-up enabled
    U1MODEbits.LPBACK = 0;              // Loopback mode is disabled
    U1MODEbits.RXINV = 0;               // U1RX IDLE state is '1'
    U1MODEbits.PDSEL = 0b00;            // 8-bit data, no parity
    U1MODEbits.STSEL = 0;               // 1 stop bit
    U1STAbits.UTXINV = 0;               // U1TX IDLE state is '1'
    U1MODEbits.ON = 1;                  // UART1 is enabled
    U1STAbits.URXEN = 1;                // UART1 receiver is enabled, don't need but just in case
    U1STAbits.UTXEN = 1;                // UART1 transmitter is enabled
}


void sendChar(char c) {
    while(U1STAbits.UTXBF);             // Wait while buffer is full
    U1TXREG = c;                        // Transmit character
}

void InitJellyfish(void) {
    // TODO send setup commands to ADS1299 
}


short ReadEEG(void) {
    short X_H = WriteReadSPI(0b1010100100000000);    // Read first data register
    short X_L = WriteReadSPI(0b1010100000000000);    // Read second data register
    X_L = X_L & 0b0000000011111111;                  // Combine the data from both registers
    X_H = X_H << 8;
    X_H = X_H & 0b1111111100000000;
    signed short X = X_H | X_L;
    return X;
}


void sendSampleDataUART() {
    int i;
    for (i = 1; i < 10; i++) {
        while(U1STAbits.UTXBF);         // Wait while buffer is full
        U1TXREG = i;
    }
}


/******************************************************************************/
/* Main Program                                                               */
/******************************************************************************/

int32_t main(void) {

#ifndef PIC32_STARTER_KIT
    /*The JTAG is on by default on POR.  A PIC32 Starter Kit uses the JTAG, but
    for other debug tool use, like ICD 3 and Real ICE, the JTAG should be off
    to free up the JTAG I/O */
    DDPCONbits.JTAGEN = 0;
#endif

    /* Initialize I/O and Peripherals for application */
    TRISDbits.TRISD1 = 0;       // make CS an output
    InitSPI();
    InitJellyfish(); 
    InitUART(); 
    short EEGsignal; 

    while(1)
    {
        // SPI transfer ----------
        EEGsignal = ReadEEG(); 
        
        // processing ------------
        // TODO turn float value stored in EEGsignal into an array to be sent over 
        // UART to a computer 
        
        // UART transfer ---------
        // Try this first. It should give a square wave ('U' in ASCII)
        sendChar('U');
        
        // If line above works try uncommenting this line, it sends array of ints
        // sendSampleDataUART();

    }
    
    return(EXIT_SUCCESS); 
}

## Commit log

2020-01-25 Added working Altium Project, and first draft of the MCU schematic
    [MCU.SchDoc, MINT_EEGAcquisitionSystem.PrjPcb]
2020-01-25 Added schematic files for power, ADS1299, and electrode interface
    [ADS1299.SchDoc, Electrode_Interface.SchDoc, MCU.SchDoc, MINT_EEGAcquisitionSystem.PrjPcb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]
2020-02-06 Finished draft of MCU schematic
    [ADS1299.SchDoc, MCU.SchDoc]
2020-02-08 updated version of the altium project
    [ADS1299.schdoc, MCU.SchDoc, PCB1.PcbDoc, PCB2.PcbDoc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]
2020-02-08 Renamed root project folder, removed some files
    [ADS1299.schdoc, EEG.PrjPcb, MCU.SchDoc, PCB1.PcbDoc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]
2020-02-08 renamed old project file for clarification
    [ADS1299.SchDoc, Electrode_Interface.SchDoc, MCU.SchDoc, MINT_EEGAcquisitionSystem.PrjPcb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]
2020-02-08 ADS 1299 Schematic Update
    [ADS1299.schdoc]
2020-02-10 updated version
    [ADS1299.schdoc]
2020-02-10 Updated ADS1299 and MCU schematics
    [ADS1299.schdoc, MCU.SchDoc, PCB3.PcbDoc, Power.SchDoc]
2020-02-10 Updated MCU schematic with surface mount components
    [EEG.PrjPcb, MCU.SchDoc]
2020-02-10 Updated ADS1299 res and caps
    [ADS1299.schdoc]
2020-02-10 Altered PCB and MCU Schematic
    [MCU.SchDoc, PCB3.PcbDoc]
2020-02-18 Added 25MHz external oscillator to MCU schematic
    [MCU.SchDoc]
2020-02-22 schematic version
    [ADS1299.schdoc, EEG.PrjPcb, MCU.SchDoc, PCB3.PcbDoc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]
2020-02-22 updated version
    pcb 3 completed
    [ADS1299.schdoc, EEG.PrjPcb, MCU.SchDoc, PCB3.PcbDoc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]
2020-02-23 Update ADS 1299 schematic
    updated the pin protection wiring
    [ADS1299.schdoc]
2020-04-03 added PCB layout images
2020-04-11 added multisim model of passive filter
2020-09-20 Added PCB layout and Gerber files for electrode Pre-Amp
    [Gerber_BoardOutline.GKO, Gerber_BottomLayer.GBL, Gerber_BottomSolderMaskLayer.GBS, Gerber_Drill_PTH.DRL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]
2020-09-20 added schdoc format
    [electrodePCB.schdoc]
2020-11-08 Rearranged folders
    [ADS1299.SchDoc, ADS1299.schdoc, EEG.PrjPcb, Electrode_Interface.SchDoc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]
2020-11-08 Add MENTHA3.0 back
    [ADS1299.SchDoc, ADS1299.schdoc, EEG.PrjPcb, Electrode_Interface.SchDoc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]
2020-11-08 Solidworks and STL files of saline-based electrode
    [Container_Lid.SLDPRT, Fluid Holder.SLDPRT, Jellyfish_Assembly1.SLDASM, New lid.SLDPRT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]
2020-11-22 Electrode summary
